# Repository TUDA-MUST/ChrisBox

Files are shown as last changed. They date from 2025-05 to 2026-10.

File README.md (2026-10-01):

# ChrisBox
(**CH**arge **R**eading **I**nferface **S**ystem Box)\
4-Channel Charge Amplifier PCB

## Introduction

Welcome to ChrisBox!\
ChrisBox is a four-channel charge amplifier, mainly developed for the simultaneous charge measurement of four ferroelectret sensors.
The main goals of the development were
- low noise (shielding concept),
- portability,
- usability,
- affordability.

More details about ChrisBox can be found [here](#about-chrisbox).

> [!IMPORTANT]
> This document describes the features and assembly of ChrisBox and does not provide guidance on constructing or using ferroelectret sensors.

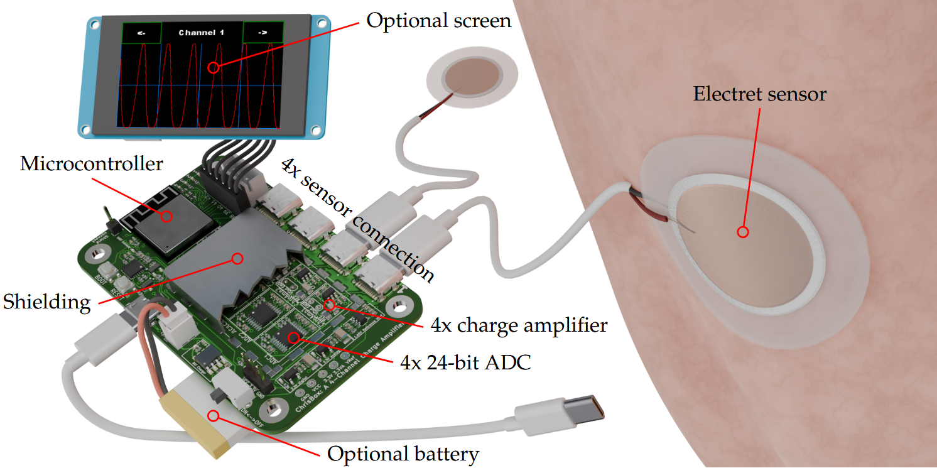
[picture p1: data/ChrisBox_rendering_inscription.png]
Rendered image of ChrisBox with display, battery and connected ferroelectret sensors.


## About this Repository

This repository contains the PCB design of ChrisBox, the CAD files for the Box, where the PCB can be combined with a battery and a display, as well as general code for the PCB.
- [PCB](/PCB) -> circuit board
- [CAD](/CAD) -> housing for the circuit board and an additional display
- [CODE](/CODE) -> code to be flashed on the microcontroller of the PCB, and code for a Nextion display.

A code description is found in the `./CODE` folder, if you just want to build a ChrisBox, the following instructions should be sufficient.

Ordering and Building instructions are included here:
- [ORDERING INSTRUCTIONS](/ORDERING_INSTRUCTIONS.md)
- [BUILDING INSTRUCTIONS](/BUILDING_INSTRUCTIONS.md)

Contributing to ChrisBox and this repository: [CONTRIBUTORS](#contributors).\
License: [LICENSE](/LICENSE).

Information about citation is found here: [CITATION](#citation).

## About ChrisBox

### Development objective and target group

Piezoelectric sensors convert electric charge in response to mechanical loading and are widely studied for their high sensitivity.
In particular, ferroelectret sensors provide the flexibility and material system design that enable biocompatibility.
These signals are typically captured using commercial electrometers or custom-built charge amplifiers to enable portability.
However, the latter often lack the precision and robustness against electromagnetic interference (EMI).
Therefore, we present a compact, four-channel portable measurement system specifically designed for charge-based force sensing with piezoelectric sensors, called ChrisBox.
The system has been developed at the **Measurement and Sensor Technology Group** at **Technische Universität Darmstadt**, Darmstadt, Germany.

The main goals of the development were:
- **Low noise:** achieved through a shielding concept that covers the PCB, the cable to the sensor, and, depending on the sensor, the sensor itself.
- **Portability:** a key advantage over traditional electrometers and oscilloscopes, enabling measurements on the human body while walking or performing other movements.
- **Usability:** the PCB is designed for users without expertise in PCB development or programming, allowing straightforward measurements with ferroelectret sensors.
- **Affordability:** one assembled PCB costs roughly 50 euros in 2025, facilitating reproduction and simultaneous use while avoiding the need for expensive laboratory instruments such as electrometers.

### Detailed decription of ChrisBox

**Analog electronics**
A ferroelectret is connected to the PCB via a USB-C cable and connector.
The signal wires, D+ and D-, carry the charge displacement generated by the ferroelectret, which is converted into a voltage signal by a charge amplifier.
An exemplary application of this setup is heart rate measurement, which requires low-frequency measurements.
Therefore, a large feedback resistor (in the G&Omega; range) is used in the charge amplifier.
A reference voltage at the midpoint of the measurement range (around 1.65 V) is provided to enable differential measurements within the 0–3.3 V range.
The analog electronics are replicated four times, with each channel operating independently.

**Digital electronics**
The output of each charge amplifier is connected to an ADC (ADS1220).
The reference voltage is also supplied to the ADC to enable differential measurements.
All four ADCs communicate with an ESP32 via SPI.

**ESP32**
An ESP32 S3 Mini 1 serves as the microcontroller of the ChrisBox, accompanied by Boot and Reset buttons.
A UART-to-USB converter ensures reliable connectivity with various PCs.

**Support circuits**
The PCB includes several additional circuits: four programmable status LEDs controlled by the ESP32, a UART connector for interfacing with a Nextion display, and a connector providing access to five GPIO pins of the ESP32 for custom functions.
A 5 V supply, switchable by the ESP32, can power the Nextion display.
A battery can be connected for power supply and is simultaneously charged when the board is connected to USB.

**Shielding**
The PCB is shielded by a metallic frame and cover, as well as an internal shielding layer within the board.
USB-C cables are used to connect the ferroelectret sensors, as they are both shielded and readily available.
Each ferroelectret sensor must be soldered to a USB-C connector.
Since an unshielded ferroelectret sensor can act as a source of noise, proper shielding is essential to ensure a low-noise measurement setup.

**Data output**
The acquired measurement data can be output in several ways:
- Serial communication to a PC,
- UART connection to a Nextion display for real-time visualization,
- ESP-NOW for wireless data transmission, requiring a second ESP32 as receiver for the data, which itself could communicate to a PC.

## Contributors

ChrisBox was developed at the [Measurement and Sensor Technology Group](https://www.etit.tu-darmstadt.de/must/) at Technische Universität Darmstadt, Germany, by:
- [Sven Suppelt](https://orcid.org/0000-0002-2338-9333)
- [Dominik Werner](https://orcid.org/0009-0001-8082-5584)
- [Alexander A. Altmann](https://orcid.org/0000-0001-5299-3620)
- [Felix Herbst](https://orcid.org/0000-0003-1480-3691)
- [Jan H. Dörsam](https://orcid.org/0000-0001-9807-6641)
- [Bastian Latsch](https://orcid.org/0000-0001-9929-5694)
- [Prof. Mario Kupnik](https://orcid.org/0000-0003-2287-4481)

## Citation

If you would like to reference the project, please cite DOI: [10.3390/hardware4040020](https://doi.org/10.3390/hardware4040020).

```
@article{hardware4040020,
  author = {Suppelt, Sven and Werner, Dominik and Altmann, Alexander Anton and Herbst, Felix and Ulmer, Lukas and Dörsam, Jan Helge and Latsch, Bastian and Kupnik, Mario},
  title = {ChrisBox: An Open-Source 4-Channel Portable Charge Amplifier for Research and Education},
  journal = {Hardware},
  year = {2026},
  volume = {4},
  number = {4},
  pages = {20},
  doi = {10.3390/hardware4040020}
}
```

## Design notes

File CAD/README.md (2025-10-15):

# CAD

Welcome to the CAD folder!
Here can basically every physical part of a ChrisBox assembly be found. The assembly is shown below.
The CAD is made with Siemens NX, and STL data is provided, e.g. for 3D printing.

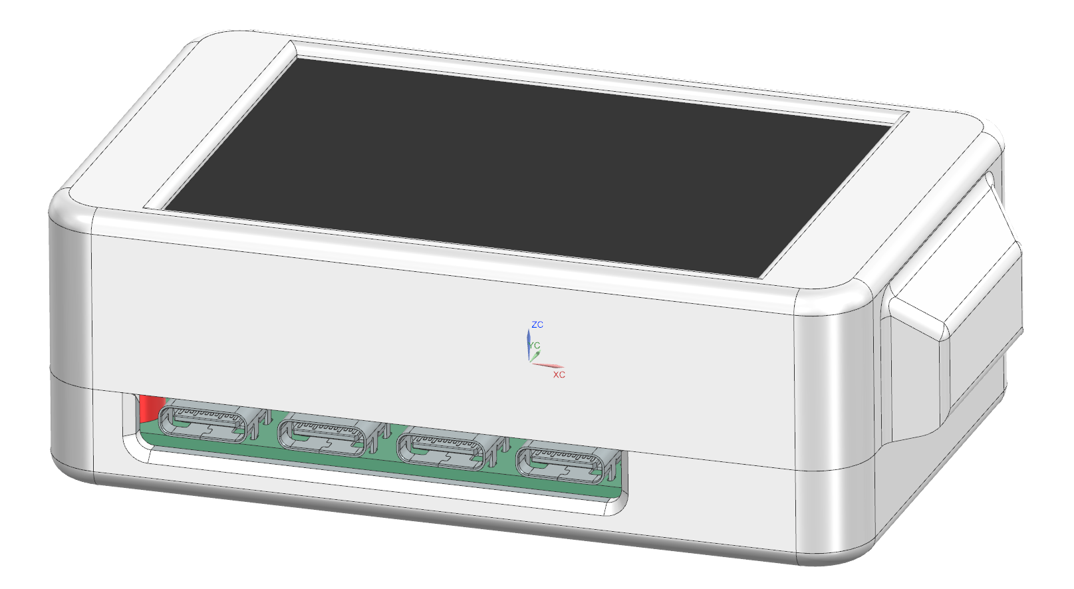
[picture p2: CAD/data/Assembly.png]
Screenshot of a ChrisBox Assembly


## Content of the CAD folder

- `./Casing` - Siemens NX part files for the casing.
- `./Electric` - Electric components of the assembly (PCB with most components, a standard Battery and the NX3224K024 display). 
- `./STLs` - STL data of the casing, e.g. for 3D printing
- `./data` - pictures of the assembly

## Building the casing

For building instructions refer to [BUILDING INSTRUCTIONS](/BUILDING_INSTRUCTIONS.md).

## Alternate Version without the Nextion screen

If you are only interested in a Chrisbox without a display, you will find a protective case for the PCB in the “00_VersionWithoutScreen” folder. 
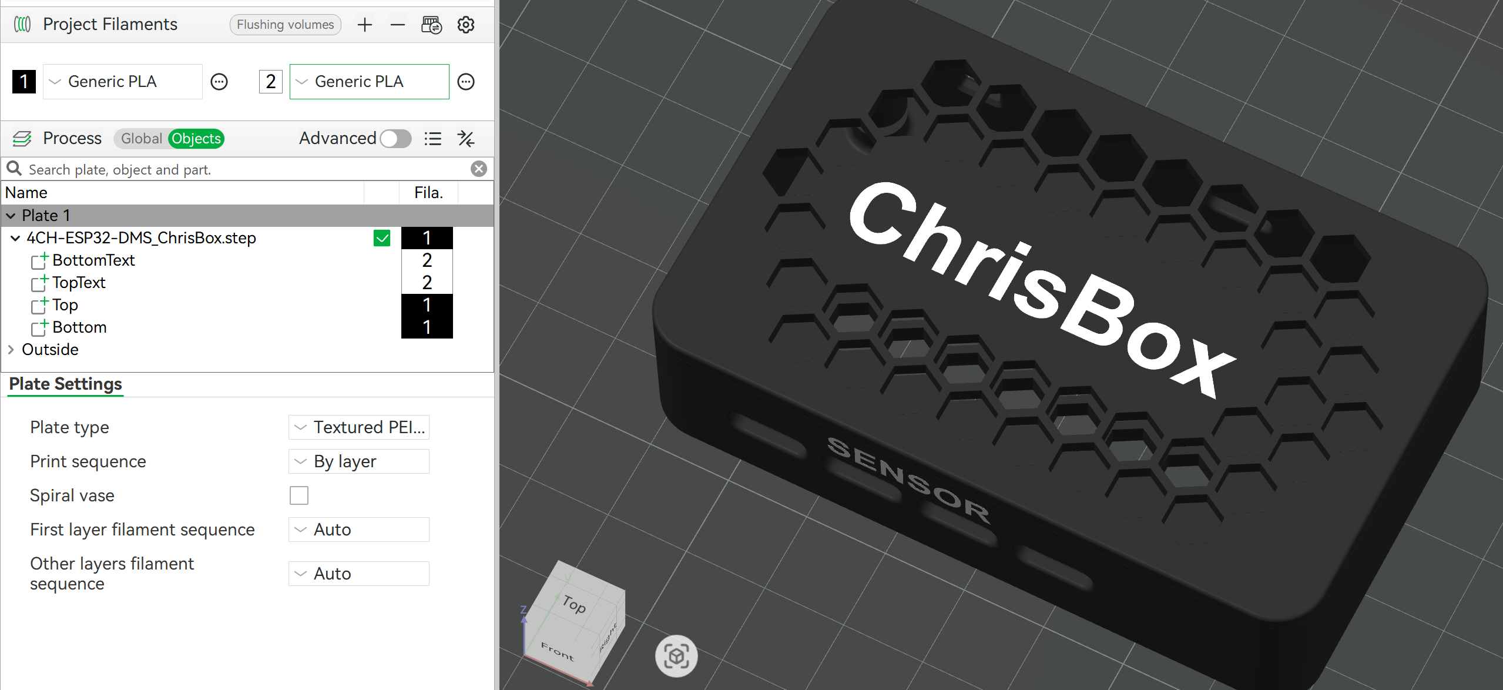
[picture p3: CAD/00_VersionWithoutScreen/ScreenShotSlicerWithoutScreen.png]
Screenshot of a ChrisBox Assembly wihtout a screen


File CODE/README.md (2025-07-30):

# Code

Welcome to the Code folder of ChrisBox!
The code for ChrisBox was written in the Arduion IDE.

## Content of the PCB folder

- `./ChrisBox_Code` - The code and librarys for the ChrisBox PCB.
- `./Nextion Code` - The code/program for the Nextion display.

## Flashing the code on the PCB

For flashing both the PCB and the Nextion display, please refer to [BUILDING INSTRUCTIONS](/BUILDING_INSTRUCTIONS.md).

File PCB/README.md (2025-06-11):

# PCB

Welcome to the PCB folder of ChrisBox!
The ChrisBox PCB is designed with KiCad. The Project files and generated Exports are found here.

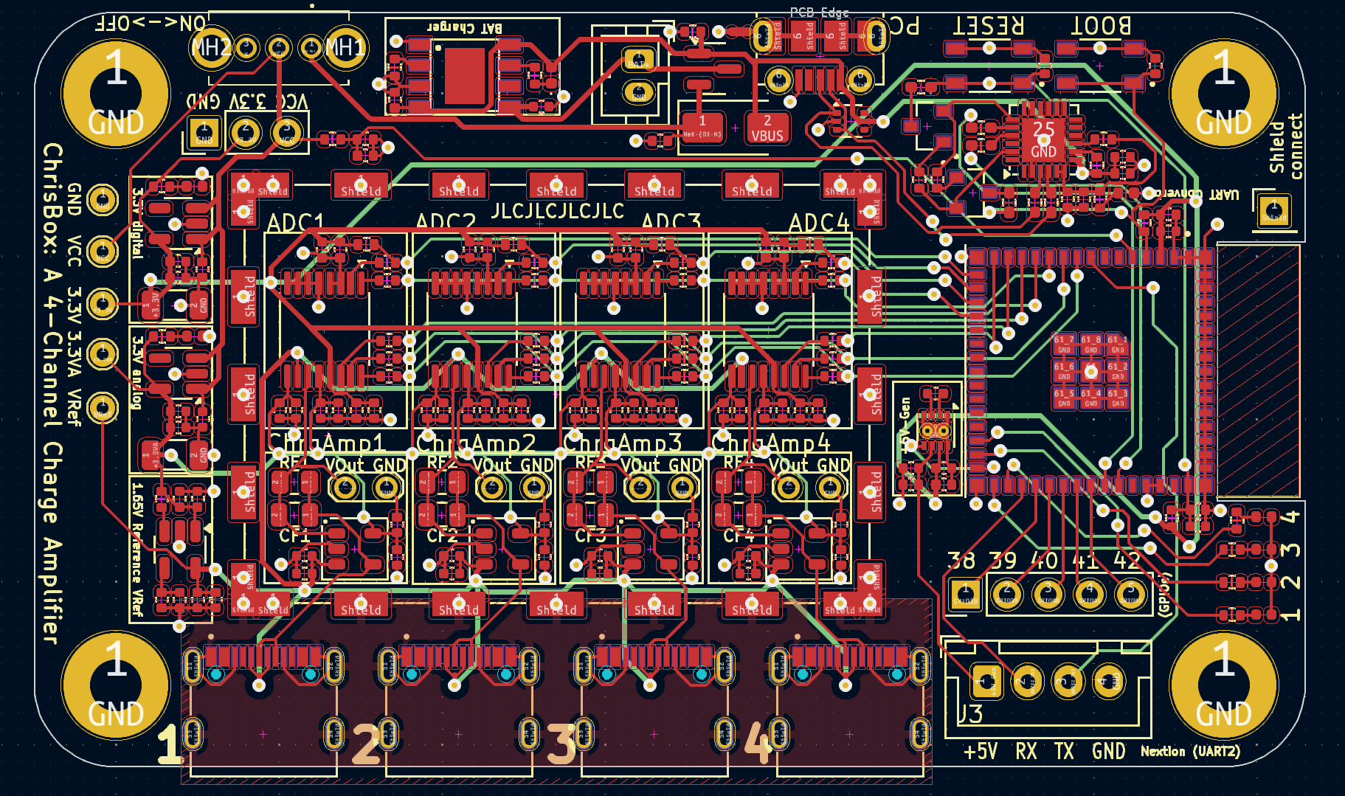
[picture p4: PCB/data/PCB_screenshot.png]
Screenshot of a ChrisBox Assembly


## Content of the PCB folder

- `./data` - pictures of the PCB and some for the schematic and silkscreen.
- `./exports` - The `.step`-export of the ChrisBox PCB.
- `./interactive bom` - The interactive HTML BOM (made with Interactive Html Bom). It is useful for handsoldering or just looking up which component has to go where.
- `./jlcpcb` - Output data from the KiCAD JLCPCB tools. This data can be used for ordering a PCB with components. Always re-check the data yourself!
- `./models` - Additional footprints and models, which are not included in KiCad and its plugins itself.

The other files in this folder are the [main KiCad project](/PCB/ChrisPCB.kicad_pro) with schematic and pcb, as well as the sub-schematics (ferro_amplifier and usb_connector).

## Notes on KiCad settings

The design was made with KiCad 8.0. Installed plugins are the Alternate KiCad Library (by Dawid Cislo), the Interactive Html Bom (by qu1ck) and the KiCAD JLCPCB tools (by Bouni).
Additional Footprints or 3D models are found in the `./models` folder.\
Always check the JLCPCB options yourself! The tools seemed to "forget" some data from time to time.

## Ordering and building the PCB

For ordering instructions refer to [ORDERING INSTRUCTIONS](/ORDERING_INSTRUCTIONS.md).
For building instructions refer to [BUILDING INSTRUCTIONS](/BUILDING_INSTRUCTIONS.md).

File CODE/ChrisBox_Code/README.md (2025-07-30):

# ChrisBox Code

In this section the main features of the ChrisBox code are explained. The code was written in Arduino IDE 2.x.x.

> [!NOTE]
> In the code the [Protocentral library for the ADS1220](https://github.com/Protocentral/Protocentral_ADS1220) is used, which also is under the MIT license. Some minor changes are made in the library to adapt the pins to the wiring of the ChrisBox PCB.

## Code structure

There are the following sections in the code:

- include for the used libraries
- definitions for pins
- some settings and constants. Settings regarding ESP NOW, UART, BAUDRate etc. are made here.
- variables, which are used at runtime
- setup for ESP NOW
- setup for UART
- void setup(). The different parts (e.g. UART) are started here, if the part is wished (see settings and constants).
- void loop(). This is repeated after the setup until the power is switched of or reset is pressed. The ADCs are read and the measured values published on the Serial port, ESP NOW and/or UART
- support functionality

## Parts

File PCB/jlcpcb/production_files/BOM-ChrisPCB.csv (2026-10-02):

Comment | Designator | Footprint | LCSC | Quantity
0 | R38,R39,R41,R42,R45,R50 | R_0402_1005Metric_Pad0.72x0.64mm_HandSolder | C17168 | 6
100n | C10,C12,C13,C18,C2,C21,C22,C23,C26,C27,C30,C33,C34,C35,C38,C39,C4,C42,C45,C46,C47,C50,C51,C54,C57,C58,C59,C6,C62,C63,C65,C67,C71,C79,C81,C9 | C_0402_1005Metric | C1525 | 36
100u | C7,C8 | C_1206_3216Metric | C15008 | 2
10k | R40,R44,R47,R49,R52,R6,R7 | R_0402_1005Metric | C25531 | 7
10u | C1,C11,C14,C16,C17,C19,C20,C24,C25,C28,C29,C3,C31,C32,C36,C37,C40,C41,C43,C44,C48,C49,C5,C52,C53,C55,C56,C60,C61,C64,C69,C70,C73,C75,C77,C80 | C_0402_1005Metric | C15525 | 36
1k | R12,R18,R24,R30,R37,R43,R48 | R_0402_1005Metric | C11702 | 7
1u | C15,C72,C74,C76,C78 | C_0402_1005Metric | C14445 | 5
2G | RF1,RF2,RF3,RF4 | R_0805_2012Metric | C2484710 | 4
360p | CF1,CF2,CF3,CF4 | C_0805_2012Metric | C5375895 | 4
4.7u | C66,C68 | C_0402_1005Metric | C23733 | 2
47 | R13,R14,R15,R16,R17,R19,R20,R21,R22,R23,R25,R26,R27,R28,R29,R3,R31,R32,R33,R34,R35 | R_0402_1005Metric | C25118 | 21
470 | R1,R2,R36,R4,R5,R51,R53 | R_0402_1005Metric | C25117 | 7
4k7 | R46 | R_0402_1005Metric | C25900 | 1
AD8605ARTZ | U10,U4,U6,U8 | SOT-23-5 | C9641 | 4
ADS1220xPW | U3,U5,U7,U9 | TSSOP-16_4.4x5mm_P0.65mm | C48263 | 4
AP2112K-3.3 | U13,U14 | SOT-23-5 | C51118 | 2
BOOT_SWITCH | S2 | SW_SKRPABE010 | C778166 | 1
CP2102N-Axx-xQFN24 | U12 | QFN-24-1EP_4x4mm_P0.5mm_EP2.6x2.6mm | C969151 | 1
Conn_01x04_Socket | J3 | JST_XH_B4B-XH-A_1x04_P2.50mm_Vertical | C144395 | 1
DMG2305 | Q3 | SOT-23 | C2940629 | 1
D_Schottky | D1 | D_SMA | C163541 | 1
ESP32-S3-MINI-1-N8 | U2 | XCVR_ESP32-S3-MINI-1-N8 | C3013941 | 1
JST-PH | X1 | JST_PH_B2B-PH-K_1x02_P2.00mm_Vertical | C131337 | 1
LED_CHRG | D9 | LED_0402_1005Metric | C2852592 | 1
LED_INFO1 | D5 | LED_0402_1005Metric | C434449 | 1
LED_INFO2 | D6 | LED_0402_1005Metric | C434449 | 1
LED_INFO3 | D7 | LED_0402_1005Metric | C2844007 | 1
LED_INFO4 | D8 | LED_0402_1005Metric | C2844007 | 1
LED_PWR1 | D2 | LED_0402_1005Metric | C2852592 | 1
LED_PWR2 | D3 | LED_0402_1005Metric | C2852592 | 1
LED_PWR3 | D4 | LED_0402_1005Metric | C2852592 | 1
LM2775DSG | U15 | WSON-8-1EP_2x2mm_P0.5mm_EP0.9x1.6mm_ThermalVias | C473361 | 1
RESET_SWITCH | S3 | SW_SKRPABE010 | C778166 | 1
RFShield_TwoPieces | J6 | Laird_Technologies_BMI-S-205-F_38.10x25.40mm_HandSolder_SelfMade | C7429170 | 1
SK-12D02-VG3 | S1 | SK12D02VG3 | C136723 | 1
SS8050-G | Q1,Q2 | TRANS_SS8050-G | C164886 | 2
TP4056 | IC1 | SOP-8 | C16581 | 1
TPS73616DBV | U1 | SOT-23-5 | C115797 | 1
TYPE-C-31-M-12 | J10,J7,J8,J9 | HRO_TYPE-C-31-M-12 | C165948 | 4
USBLC6-2P6 | U11 | SOT-666 | C2827693 | 1
USB_B_Micro | J11 | USB_Micro-B_Molex-105017-0001 | C505111 | 1
Conn_01x05_Pin | J2 | PinHeader_1x05_P2.54mm_Vertical |  | 1
TestPoint | TP1 | TestPoint_THTPad_D1.5mm_Drill0.7mm |  | 1
TestPoint | TP5 | TestPoint_THTPad_D1.5mm_Drill0.7mm |  | 1
TestPoint | TP3 | TestPoint_THTPad_D1.5mm_Drill0.7mm |  | 1
Conn_01x01_Pin | J5 | PinHeader_1x01_P2.54mm_Vertical |  | 1
Conn_01x03_Pin | J1 | PinHeader_1x03_P2.54mm_Vertical |  | 1
TestPoint | TP4 | TestPoint_THTPad_D1.5mm_Drill0.7mm |  | 1
TestPoint | TP2 | TestPoint_THTPad_D1.5mm_Drill0.7mm |  | 1

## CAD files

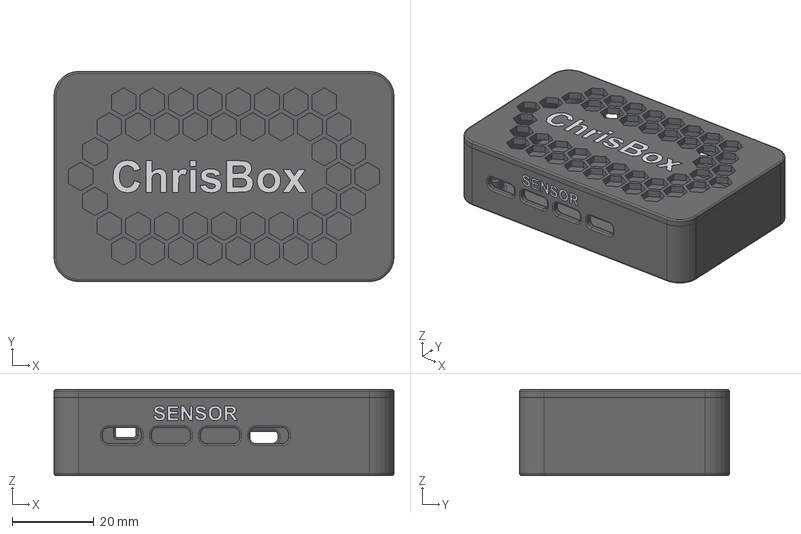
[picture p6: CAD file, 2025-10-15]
CAD/00_VersionWithoutScreen/4CH-ESP32-DMS_ChrisBox.step
83.0 x 51.3 x 21.0 mm
BottomText
TopText
Top
Bottom

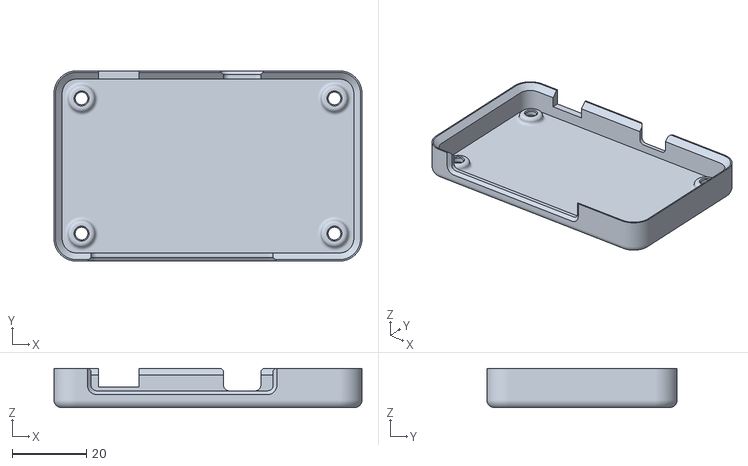
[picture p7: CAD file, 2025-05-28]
CAD/STLs/Casing_Bottom.stl
82.8 x 51.1 x 10.5

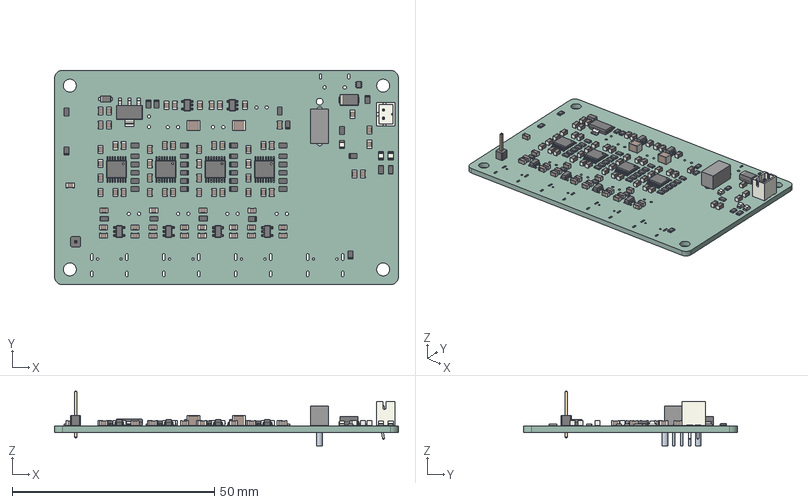
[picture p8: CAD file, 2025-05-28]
PCB/exports/ChrisPCB.step
85.0 x 53.0 x 13.5 mm
R_0805_2012Metric x 40
C_1210_3225Metric x 2
ASSEMBLY
SOT_23_5 x 6
C_0805_2012Metric x 69
D_SMA
TSSOP_16_44x5mm_P065mm x 4
LED_0805_2012Metric x 3
SOT_666
SOT_223
D_SOD_123F
JST_B2B_PH_K
PinHeader_1x01_P254mm_Vertical
Platine 4 Kanal Ferroelektret_PCB

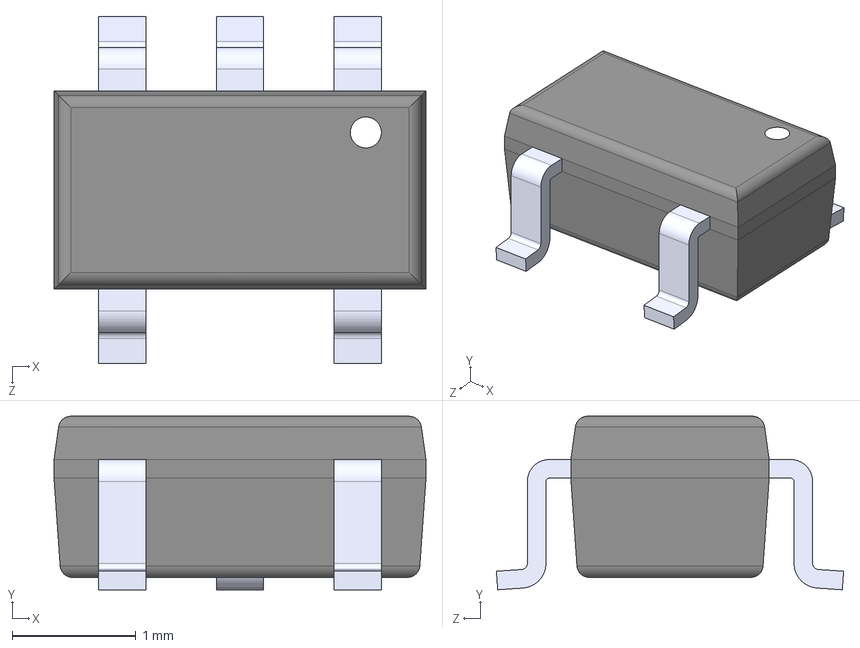
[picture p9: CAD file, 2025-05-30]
PCB/models/AP2112K-3.3TRG1/AP2112K-3.3TRG1.step
3.00 x 1.40 x 2.80 mm

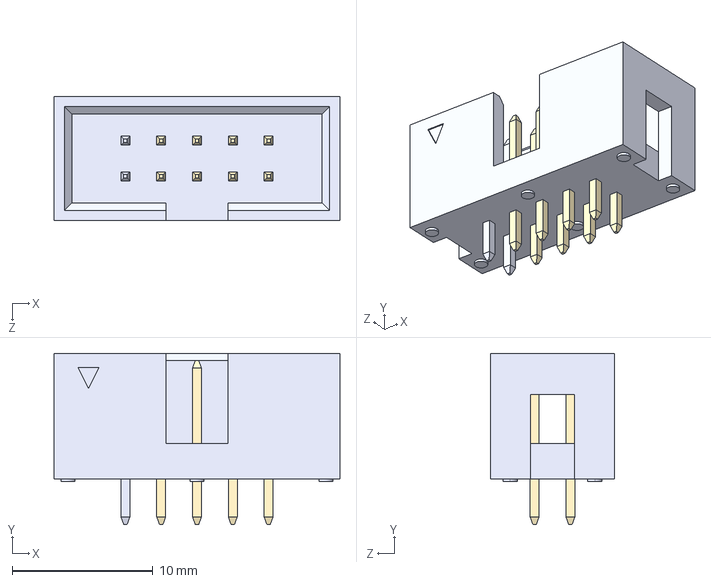
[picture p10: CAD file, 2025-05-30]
PCB/models/DC3 10P/302-S-10-D1R1.step
20.3 x 12.2 x 8.80 mm

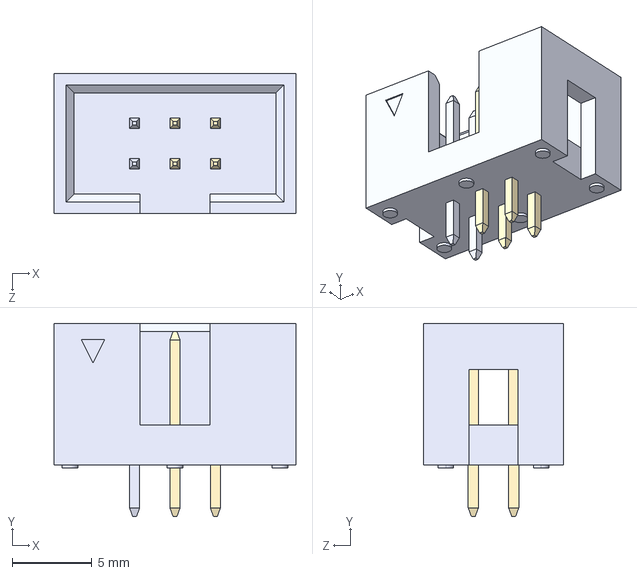
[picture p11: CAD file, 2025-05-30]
PCB/models/DC3 6P/302-S-06-D1R1.step
15.2 x 12.2 x 8.80 mm

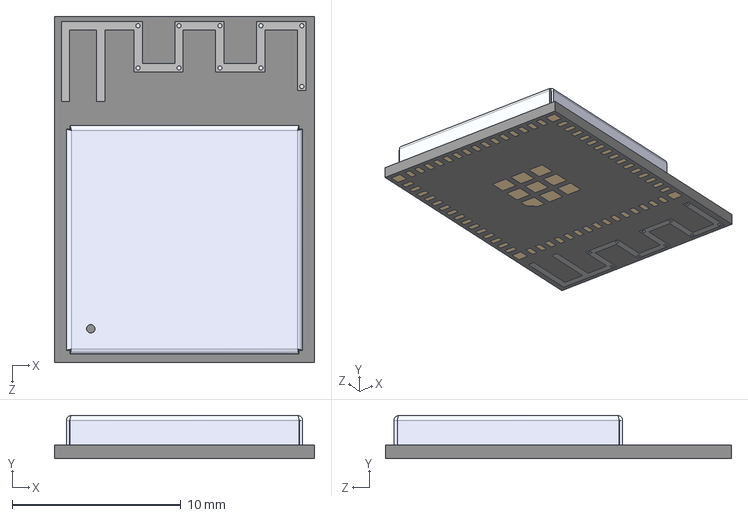
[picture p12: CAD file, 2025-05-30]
PCB/models/ESP32-S3-MINI-1-N8/ESP32-S3-MINI-1-N8.step
15.4 x 2.55 x 20.5 mm

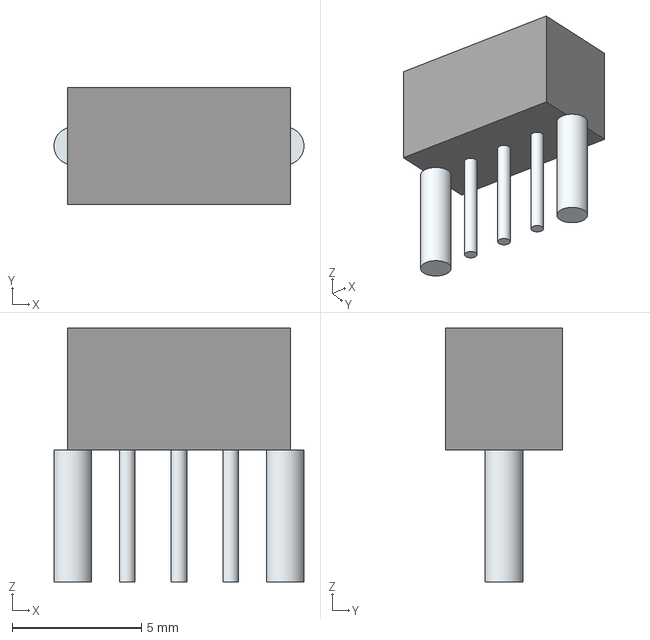
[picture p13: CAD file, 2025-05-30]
PCB/models/SK-12D02-VG3/SK-12D02-VG3.stp
9.65 x 4.50 x 9.80 mm
Leads x 5

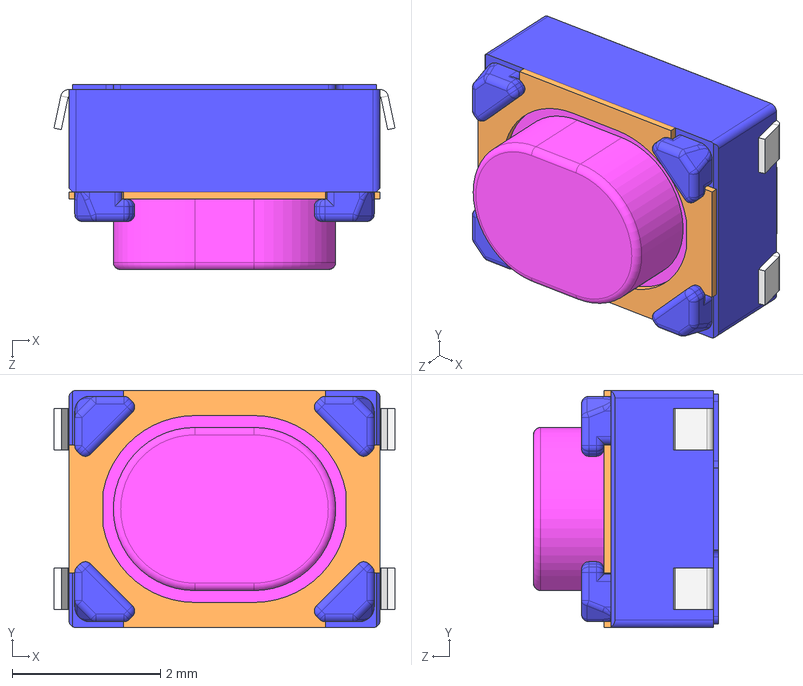
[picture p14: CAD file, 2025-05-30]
PCB/models/SKRPAB.STEP
4.60 x 3.20 x 2.50 mm

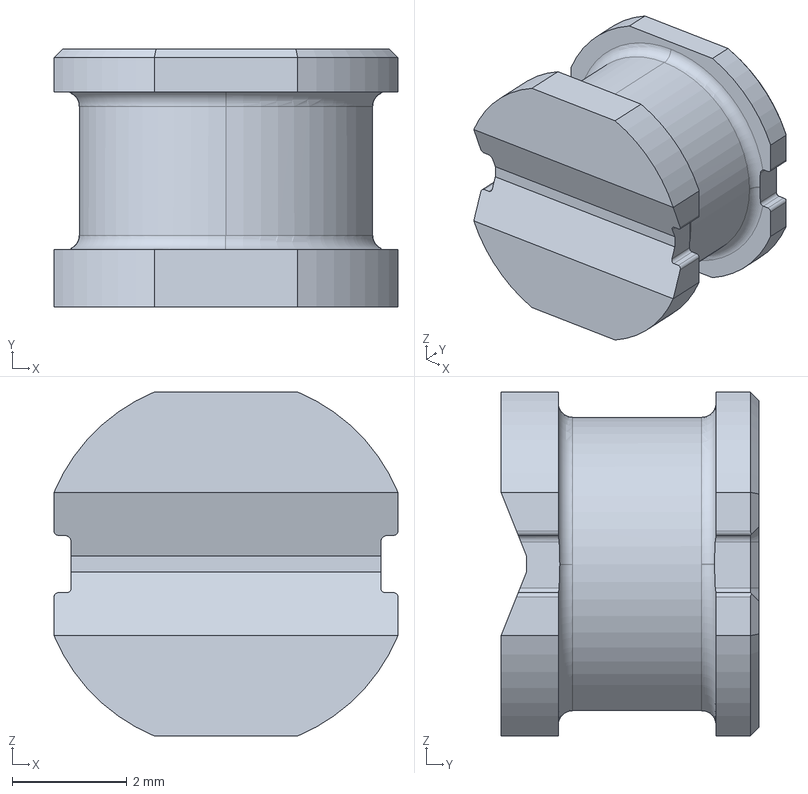
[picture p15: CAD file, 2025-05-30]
PCB/models/SRN6045-330M/SRN6045-330M.step
6.00 x 4.50 x 6.00 mm

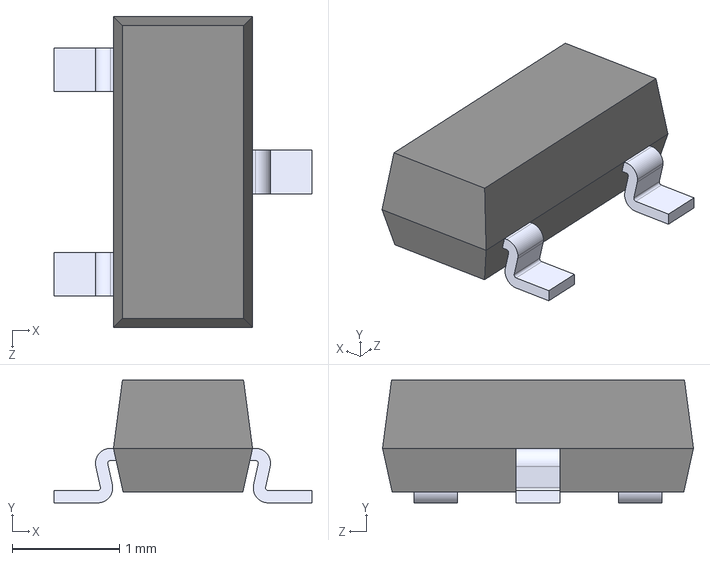
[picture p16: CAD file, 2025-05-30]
PCB/models/SS8050-G/SS8050-G.step
2.40 x 1.14 x 2.90 mm

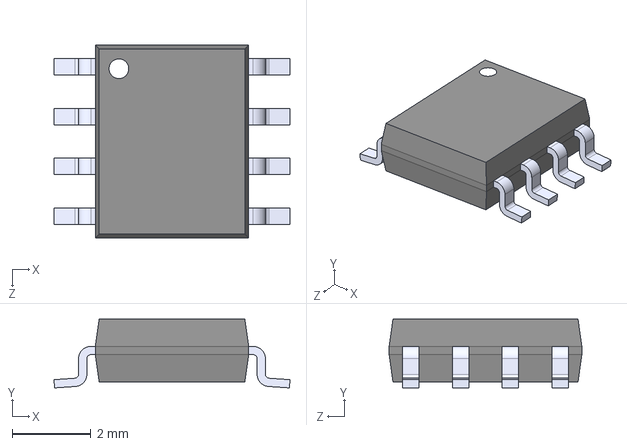
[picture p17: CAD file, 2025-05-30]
PCB/models/TP4056/TP4056.step
6.00 x 1.75 x 4.90 mm

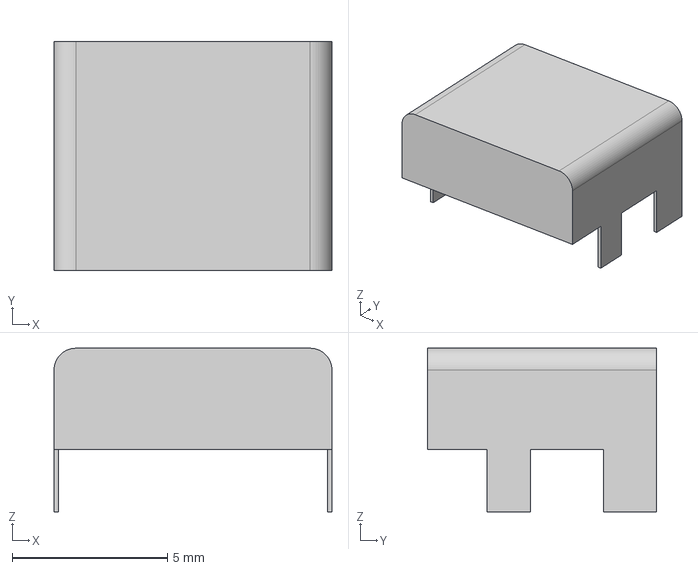
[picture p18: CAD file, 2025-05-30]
PCB/models/TYPE-C-31-M-12/TYPE-C-31-M-12 v1.step
8.94 x 7.35 x 5.26 mm

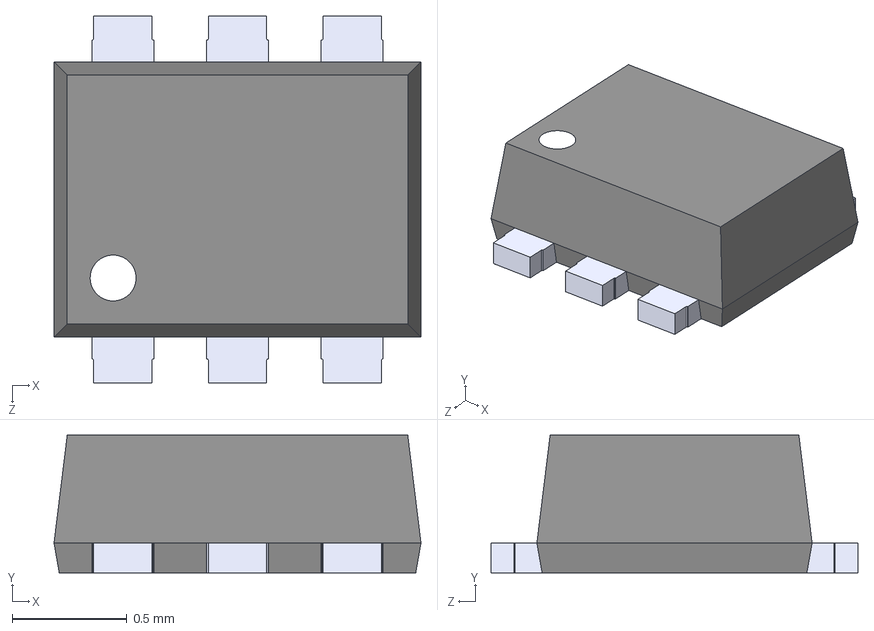
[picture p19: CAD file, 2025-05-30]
PCB/models/USBLC6-2P6/USBLC6-2P6.step
1.60 x 0.6 x 1.60 mm

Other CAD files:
PCB/models/SKRPABE010/SKRPABE010.step
CAD/STLs/Spacer.stl
PCB/models/TYPE-C-31-M-12--3DModel-STEP-56544.STEP
PCB/models/TYPE-C-31-M-12/TYPE-C-31-M-12.step
CAD/STLs/Casing_Top.stl
PCB/models/BMI-S-230-F-R.STEP
PCB/models/Molex USB 1050170001/1050170001.stp
PCB/models/TP4056-42-ESOP8.STEP

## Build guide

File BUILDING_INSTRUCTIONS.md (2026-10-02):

# Building Instructions

This are the building instructions for a complete ChrisBox setup. A complete setup includes not only the main PCB and its software, but also a Nextion display and a casing. The display and casing are optional for functionality.

1. [PCB Hardware](#pcb-hardware)
2. [PCB Software](#pcb-software)
3. [Nextion Software](#nextion-software)
4. [Full ChrisBox Assembly](#full-chrisbox-assembly)

## PCB Hardware

When ordering a populated circuit board (e.g. from JLCPCB), the result should look like this:

Unsoldered version of ChrisBox

This PCB is not finished.
The shielding frame and G&Omega; feedback resistors for the charge amplifiers are typically not in stock at JLCPCB.
If you did not use their Global Sourcing Parts Service, these components are not assembled and have to be placed by hand:
- Feedback resistors: 4x 0805 (in) or 2012 (mm), 5G&Omega;
- Shield frame: 1x Laird Technologies, BMI-S-205-F
- Shield cover: 1x Laird Technologies, BMI-S-205-C

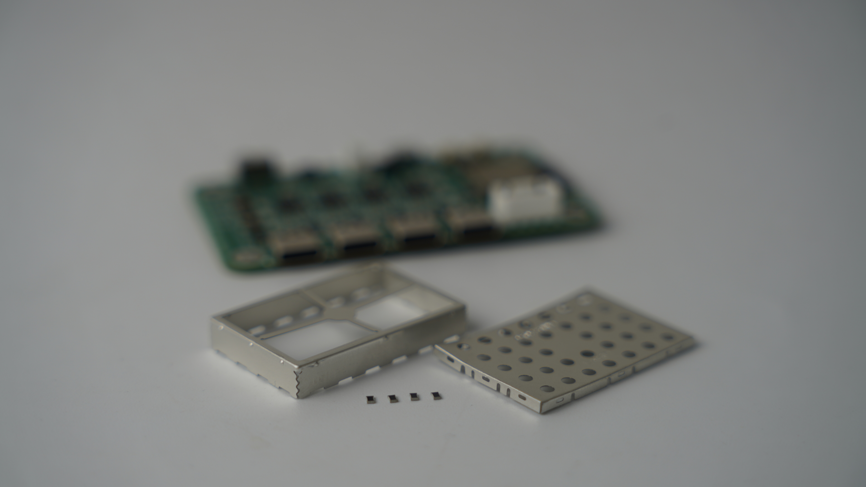
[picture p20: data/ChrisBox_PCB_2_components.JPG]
ChrisBox components for soldering


The places for the feedback resistors and the shielding frame are shown in the picture below. The shielding cover does not have to be soldered, it can be placed on the fence afterwards.
> [!TIP]
> Things get easier if the resistors are soldered first because of the height of the components.
> Also it can come handy to remove the cross in the middle of the shielding frame before soldering if some components have to be reached afterward.

Unfortunately, the frame and connected shielding plane (in the PCB) are good in heat distribution.
Therefore it takes a while to heat the pads and solder the frame.

> [!WARNING]
> When soldering, try to use as little flux as possible and/or clean the circuit board afterward. Flux is slightly conductive and distorts the sensor values, which can result in saturation of the ADC inputs!

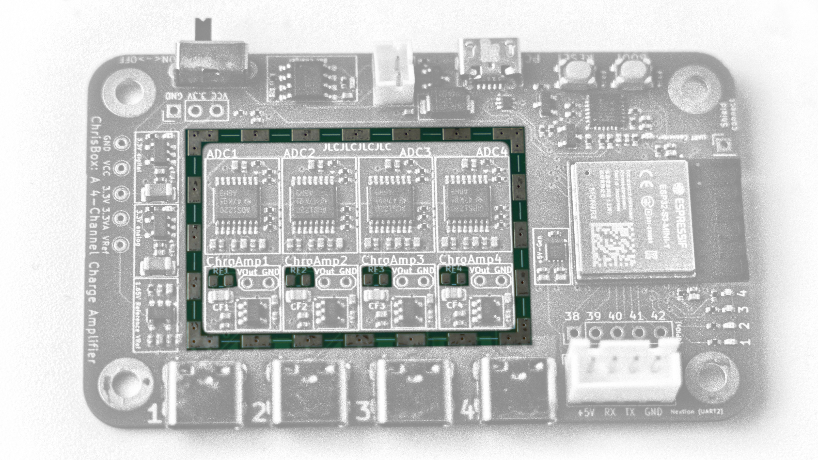
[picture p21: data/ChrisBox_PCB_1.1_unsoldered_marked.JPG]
ChrisBox places of soldering


The soldered resistors and frame can look like in the picture below. The soldering part of the PCB is finished now!

Soldered version of ChrisBox

## PCB Software

On the PCB is an ESP32-S3 microcontroller (ESP32-S3-MINI-1). The connection between PC and microcontroller works with a UART-TO-USB bridge (CP2102N). This is the same bridge chip as on most ESP32 development boards. To enable interaction between a PC and the microcontroller on the ChrisBox PCB, the **Silicon Labs CP210x USB to UART Bridge** driver should be installed on the PC.
After installing the driver, connect the ChrisBox PCB to the PC via micro USB cable and turn it on with the switch on the side. Before turing on one LED should work, after turning on multiple LEDs.
The PC should detect a device called something like "Silicon Labs CP210x USB to UART Bridge" on a COM port. Remember this COM port!

Programming works with the **Arduino IDE**. Programming and the setting were tested with Arduino IDE 2.3.6, but other versions should work as well.
In the Arduino IDE, select the device as in the picture below. Select the COM port accordingly to the one your PCB is connected to.
It may be necessary to install the esp32 by Espressif Systems via the Boards Manager.

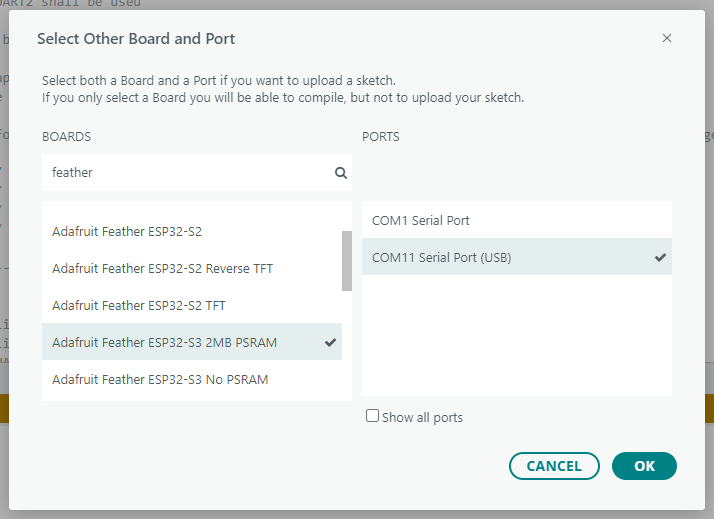
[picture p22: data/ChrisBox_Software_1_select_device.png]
Arduino IDE select device


Open the downloaded code in the Arduino IDE. It is important that all code files from this repository are in the same folder after downloading, that the Arduino IDE can find libraries while compiling.
Select the upload options as shown below and hit upload. This can take a while. After finishing, the ESP reboots and the uploaded program starts. While a program is running, a LED is blinking on the PCB.
You can see measurement data incoming on the serial monitor (select baud rate 115200). This serial data also can be viewed in the **Better Serial Plotter** or tools like **MATLAB**.

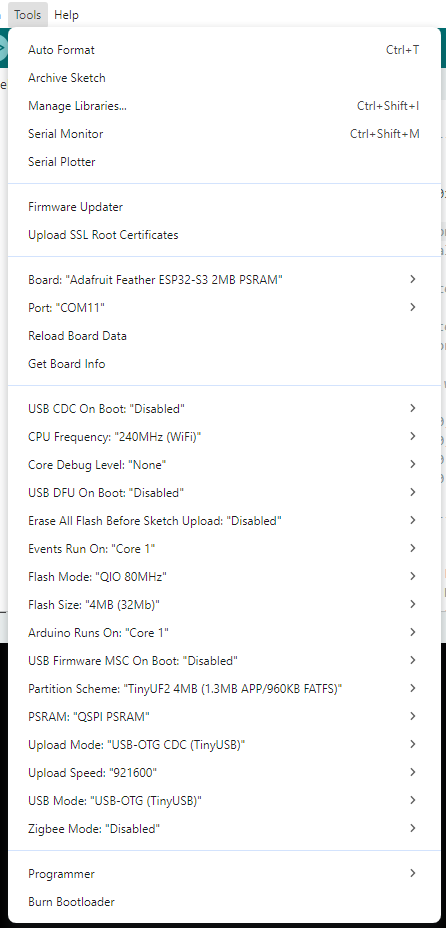
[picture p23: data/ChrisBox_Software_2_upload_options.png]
Arduino IDE upload options


## Nextion Software

The used Nextion display is a NX3224K024 display. The `.HMI` file with the code for the Nextion Editor is in the `./CODE` folder, as well a the `.tft` file. This `ChrisBox Nextion.tft` file can be flashed on a NX3224K024 display via micro SD card.
Either you open the `.HMI` file in Nextion Editor and execute a TFT file output, or you just take the given `.tft` file:
1. Save the `.tft` file to a fresh micro SD card.
2. Insert this micro SD card into the Nextion display.
3. turn on power for the display (by connection GND and 5V, either to the USB adapter or to the ChrisBox PCB.)
4. Software update starts automatically, wait for finish.
5. Turn off the power.
6. Remove SD card.
7. The update is complete. By turning power on again the loaded program should be active, without SD card!

## Full ChrisBox Assembly

The full ChrisBox assembly consists of:
- ChrisBox PCB with shielding cover
- Nextion NX3224K024 display
- cable between PCB and display
- 1x Casing Top (3D printing)
- 1x Casing Bottom  (3D printing)
- 4x Spacer (3D printing)
- 4x M3x25 screw
- 4x Threaded insert M3x3,0 (CAD made for: hole diameter 4mm, blind hole depth min. 4mm)

ChrisBox Assembly parts overview

First, insert the threaded inserts into the top of the casing with a solder iron or threaded insert heat press.

<p align="center">
      
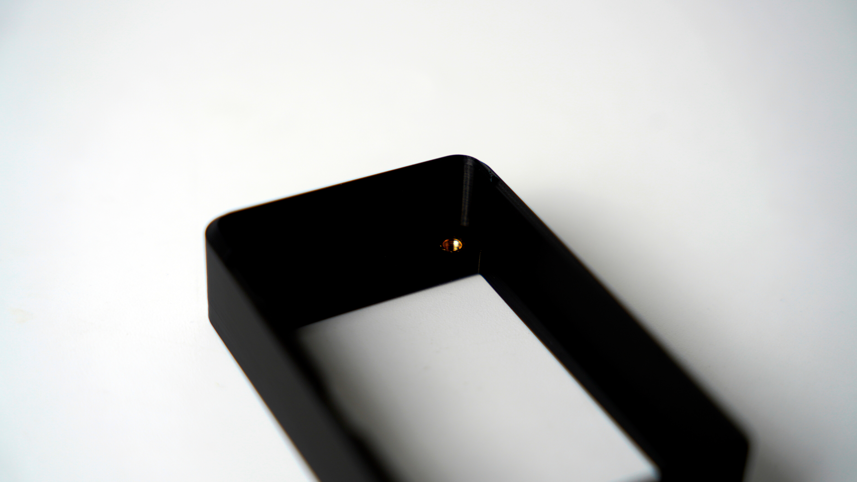
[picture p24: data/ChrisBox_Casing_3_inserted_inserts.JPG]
      
</p>

Then connect the Nextion display to the ChrisBox PCB. An ordered Nextion display contains a cable with on JST XH connector (the white 4x1 connector) and four Dupont connectors (the black 1x1 connectors).
Connect the JST XH connector to the display. You can connect the Dupont cables on the ChrisBox PCB, or you can shorten the cables and add crimp connections for another JST XH connector. This is what is used here on the picture. The JST XH connector fits directly onto the ChrisBox PCB.
Anyway, connect GND to GND, 5V to 5V and RX to TX and the other way around.
Place the shielding cover onto the shielding frame on the PCB.

Place the display into the top half of the casing, with the connector in the direction of the bulge.

<p align="center">
      
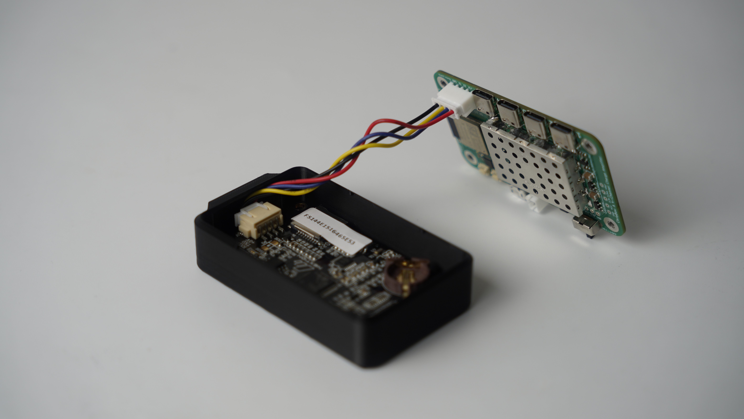
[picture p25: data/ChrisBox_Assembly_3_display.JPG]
      
</p>

Place the PCB into the bottom half of the casing, with screws and spacers.

Then connect both halves of the casing and tighten the screws. The ChrisBox is finished!

> [!TIP]
> Place the top half on top of the lower half with the screws and spacers on a table. Then move the assembly to the edge of the table that one screw can be tightened. Repeat for the other screws.

<p align="center">
      
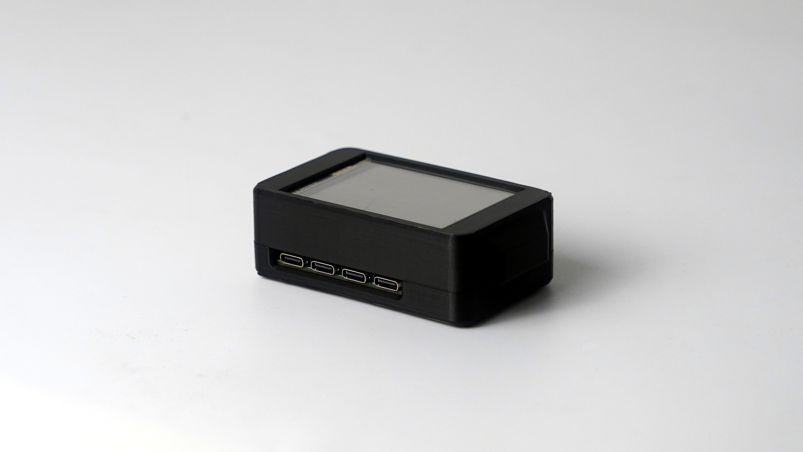
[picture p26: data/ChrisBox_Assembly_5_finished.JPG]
      
</p>

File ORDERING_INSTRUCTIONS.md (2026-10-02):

# Ordering Instructions

In this document information about the ordering process of various components can be found. This is segmented in the core PCB, required components for the PCB and additional material for a full ChrisBox setup.
It is recommended to read the other documents in this repository before ordering, as provided explanations about the different components ensure understanding of the ChrisBox and help avoiding mistakes in the ordering process.

- [README](/README.md)
- [BUILDING INSTRUCTIONS](/BUILDING_INSTRUCTIONS.md)

## PCB

The PCB is designed for ordering at JLCPCB.
Files are prepared for a populated PCB.
These files are made with the [JLCPCB Tool](https://github.com/bouni/kicad-jlcpcb-tools) in KiCad.
Keep in mind that not all components on the PCB are in stock at JLCPCB, so they have to be ordered separately (feedback resistors and shield).
Those parts can either be shipped by you to JLCPCB in advance using their [Global Sourcing Parts Service](https://jlcpcb.com/help/article/how-to-use-jlcpcb-global-sourcing-parts-service) or be manually assembled afterward, as described in the [building instructions](/BUILDING_INSTRUCTIONS.md).

The files are found in `./PCB/jlcpcb`. The gerber-files contain information about the raw PCB, the production-files contain the information about components and their positions on the PCB. The ordering process should look similar to the following screenshots:

> [!NOTE]
> The voltage generation for VRef (U1) is planned to be 1.6V in the schematic. In the JLCPCB tool and therefore in the exported data a 1.8V model is used due to production capability (at the time of data export). A reference voltage apart from 1.65V is no problem due to the differential measurement, but is shifts the measurement range so that "zero" is not in the middle and more positive or negative values can be measured.

<p align="center">
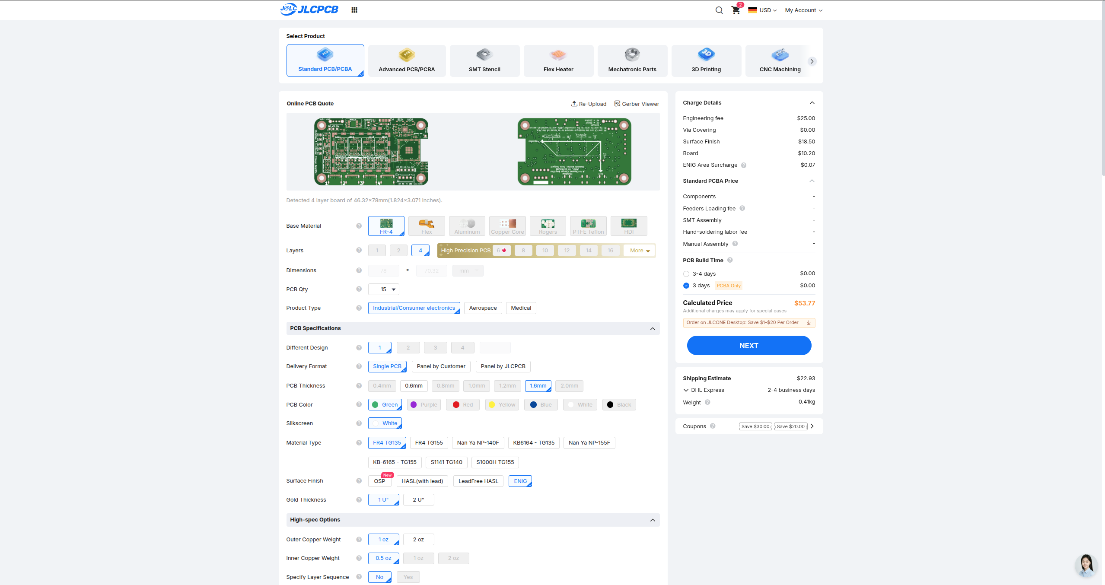
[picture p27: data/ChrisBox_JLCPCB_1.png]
      
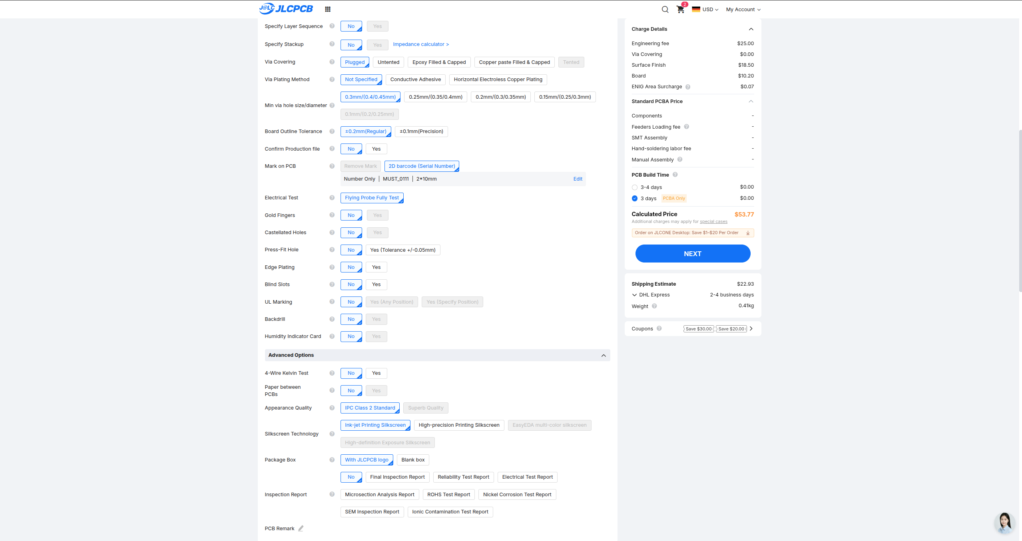
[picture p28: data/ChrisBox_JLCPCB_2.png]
      
</p>

In the ordering process, select the option "Mark on PCB", "2D Barcode (Serial Number)", "Number Only", and "Specify Position" if you want to place a serial number on your PCB.
The silkscreen contains a 2x10mm square for this purpose.
The older order number setting has been superseded.
More information about this topic can be found in the [JLCPCB instructions on PCB marks](https://jlcpcb.com/help/article/How-to-mark-on-PCB).

<p align="center">
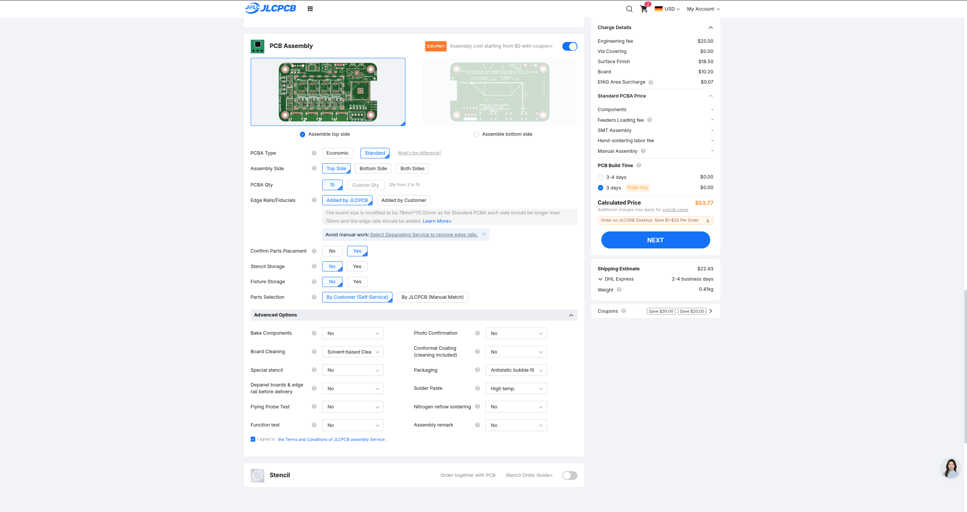
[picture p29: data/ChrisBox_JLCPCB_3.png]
      
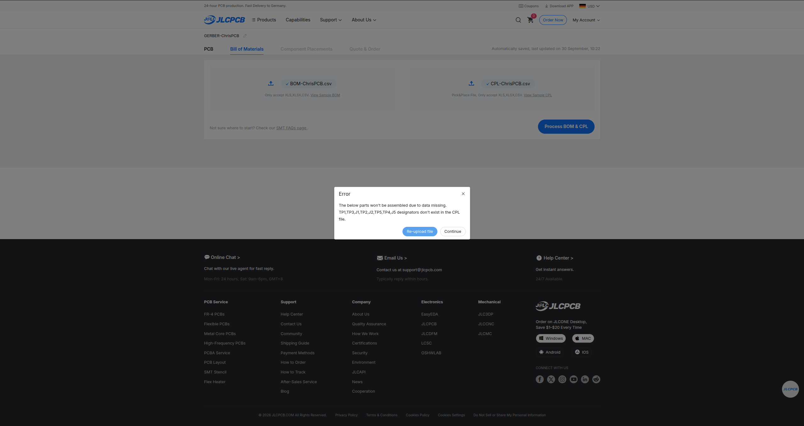
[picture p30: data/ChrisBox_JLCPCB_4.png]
      
</p>

You can also choose Economic PCBA Type here.
However, it may be possible that you are required to upgrade in the next steps.

A few optional solder headers (J1, J2, J5) and test points (TP1-TP5) purposely create an error during BOM/CPL processing, as they are part of the BOM but not in the CPL file.
Furthermore, a few lines in the BOM create warnings.
You will want to manually select all components in the list.
At the time of ordering, placement of the ESP32 module requires an upgrade from Economic to Standard Assembly.
You will need to confirm this message as well.
> [!NOTE]
> Please note that all parts have been pre-ordered through JLCPCBs [Global Sourcing Parts Service](https://jlcpcb.com/help/article/how-to-use-jlcpcb-global-sourcing-parts-service) in the screenshots.
> If you did not do so, the G&Omega; feedback resistors and shield will most likely not be available and cannot be placed.

<p align="center">
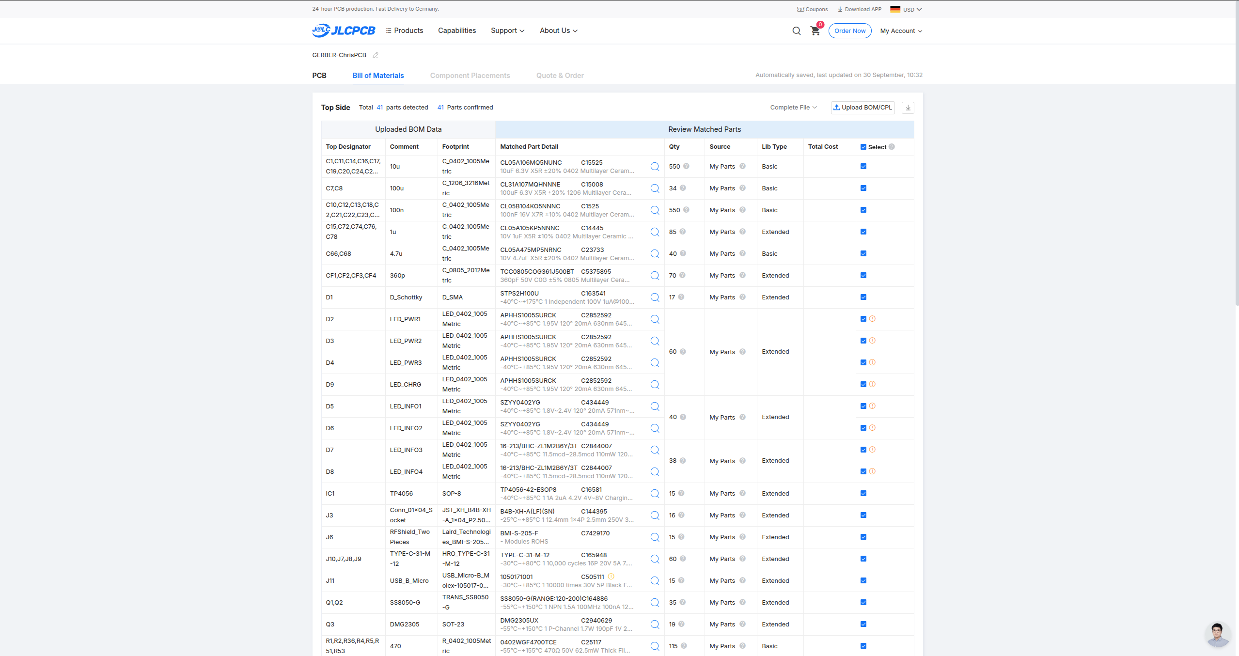
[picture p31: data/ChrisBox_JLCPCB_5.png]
      
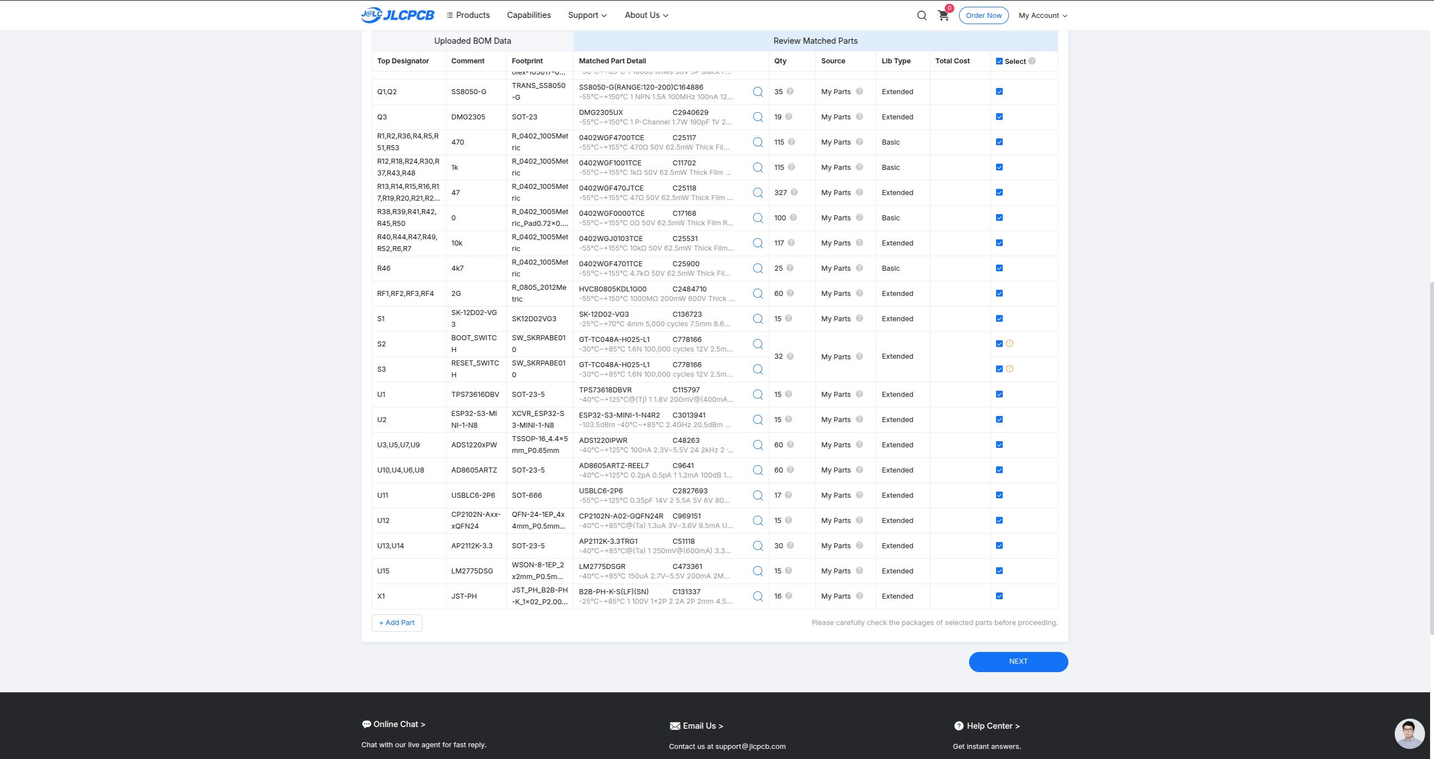
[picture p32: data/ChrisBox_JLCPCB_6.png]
      
</p>

<p align="center">
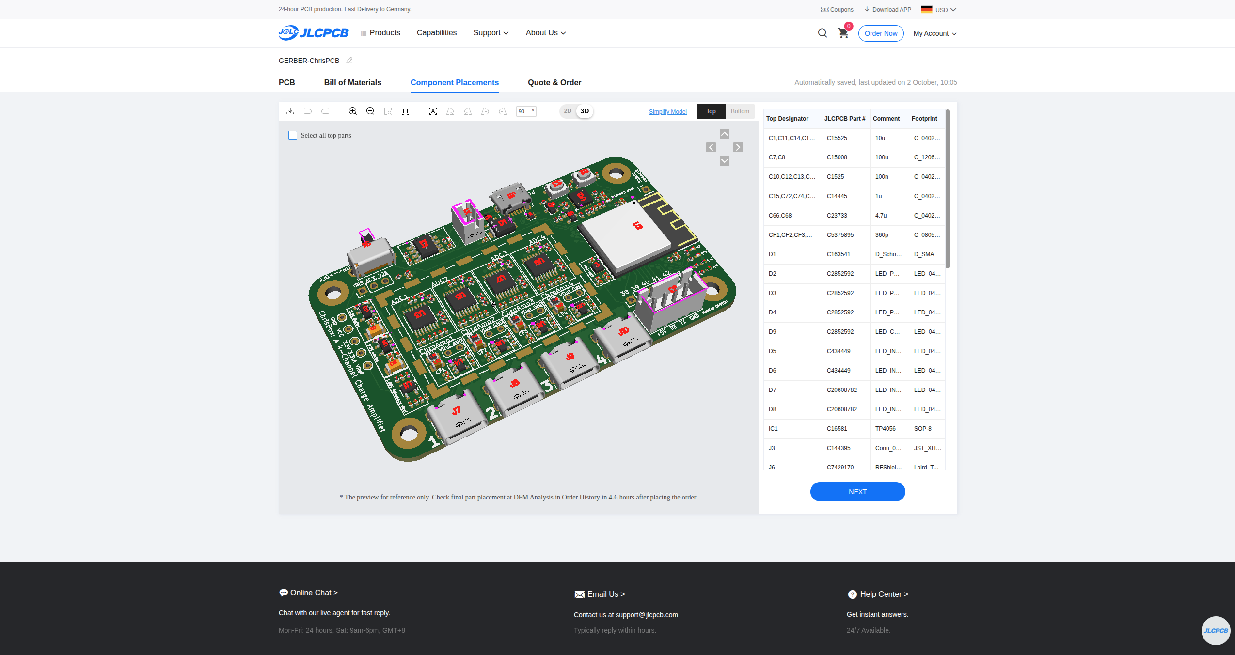
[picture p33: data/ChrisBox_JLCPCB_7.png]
      
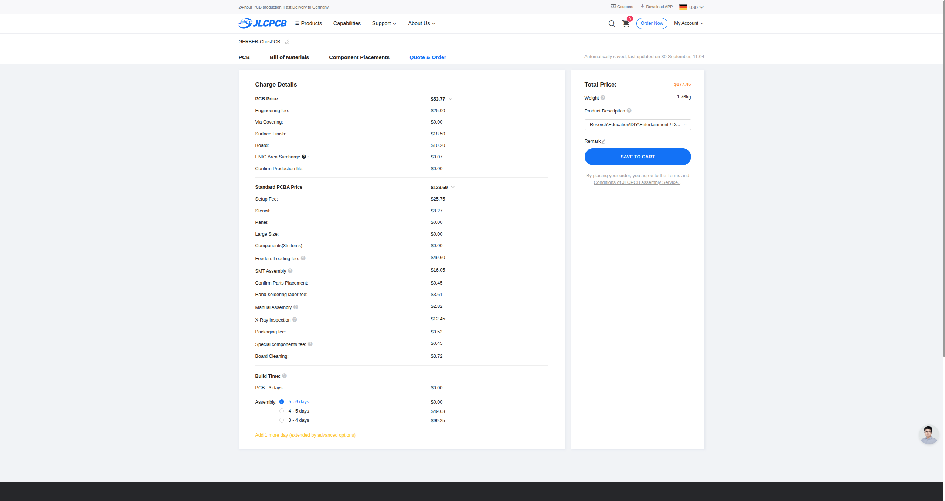
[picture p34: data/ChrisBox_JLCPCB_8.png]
      
</p>

## Additional Required Parts

### Parts for PCB

- [**4x Resistor 5G&Omega;**](https://www.digikey.com/en/products/detail/te-connectivity-passive-product/RH73W2A5GNTN/2366071), footprint 0805 (RH73W2A5GNTN, TE Connectivity).
The value of the feedback resistor decides about the low cutoff frequency of the charge amplifier.
Feel free to choose different values here if other frequencies are required.
- [**1x BMI-S-205-F**](https://www.digikey.com/en/products/detail/laird-technologies-emi/bmi-s-205-f/2175892
) and [**1x BMI-S-205-C**](https://www.digikey.com/en/products/detail/laird-technologies-emi/bmi-s-205-c/2175918
) (Shield Laird Technologies, F for frame, C for cover).
These are two different pieces, one to be soldered on the PCB, the other to be stacked above.

### Parts for Basic Measurement Setup

- [**4x USB-C cable**](https://www.amazon.de/Amazon-Basics-USB-Type-Cable-White/dp/B01GGKZ0V6/) to connect up to four sensors to the PCB
- [**USB-C female connectors/adapters**](https://www.amazon.de/PENGLIN-Stecker-Adapter-Dr%C3%A4hten-Support-Modul/dp/B09YLVSPQX/) for sensors (number depending on the amount of sensors you work with). Important is USB 2.0 functionality, which means that there are D+ and D- connections to solder the ferroelectret to. A shield around the sensor can be soldered to the housing of the adapter.
- [**Micro USB cable**](https://www.amazon.de/Amazon-Basics-%C3%9Cbertragungsgeschwindigkeit-vergoldeten-Steckern/dp/B0711PVX6Z/) to connect the PCB to a PC

## Full ChrisBox Setup

- [**1x Nextion NX3224K024**](https://nextion.tech/datasheets/nx3224k024/) Display
- A 720mAh 3.7V Lithium Polymer battery with JST PH Plug
- 3D prints for the casing (these are probably no parts to be ordered, but to be printed in lab/at home)
- [**4x threaded insert**](https://cnckitchen.store/de/products/heat-set-insert-m3-x-3-short-version-100-pieces) M3 x 3,0 (the CAD has a blind hole of 4mm, and a diameter of 4mm)
- [**4x screw**](https://www.amazon.de/Sechskopf-Knopf-Zylinderschrauben-Gewindeschrauben-Sechskantschrauben-Maschinenschrauben/dp/B0B3MGZ7T2/) M3x25 (the specific choice of screw head is not relevant, but the CAD was theoretically designed for countersunk heads)

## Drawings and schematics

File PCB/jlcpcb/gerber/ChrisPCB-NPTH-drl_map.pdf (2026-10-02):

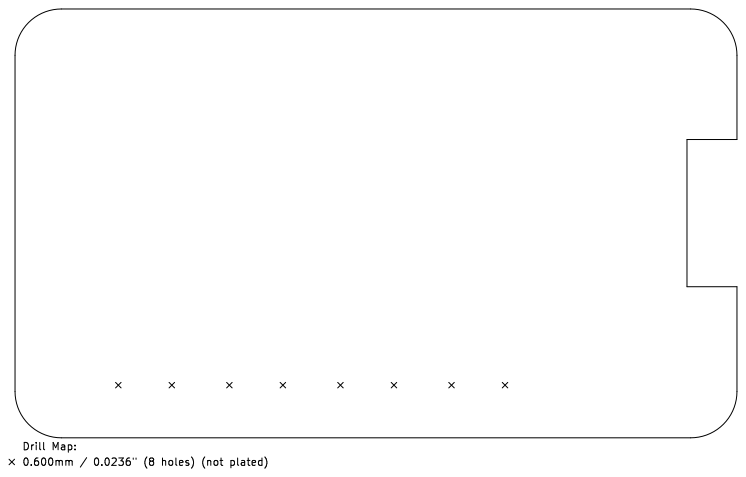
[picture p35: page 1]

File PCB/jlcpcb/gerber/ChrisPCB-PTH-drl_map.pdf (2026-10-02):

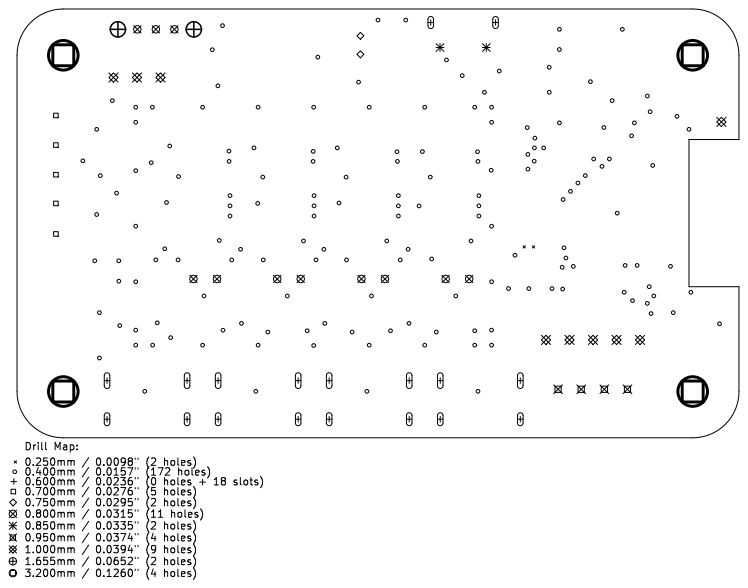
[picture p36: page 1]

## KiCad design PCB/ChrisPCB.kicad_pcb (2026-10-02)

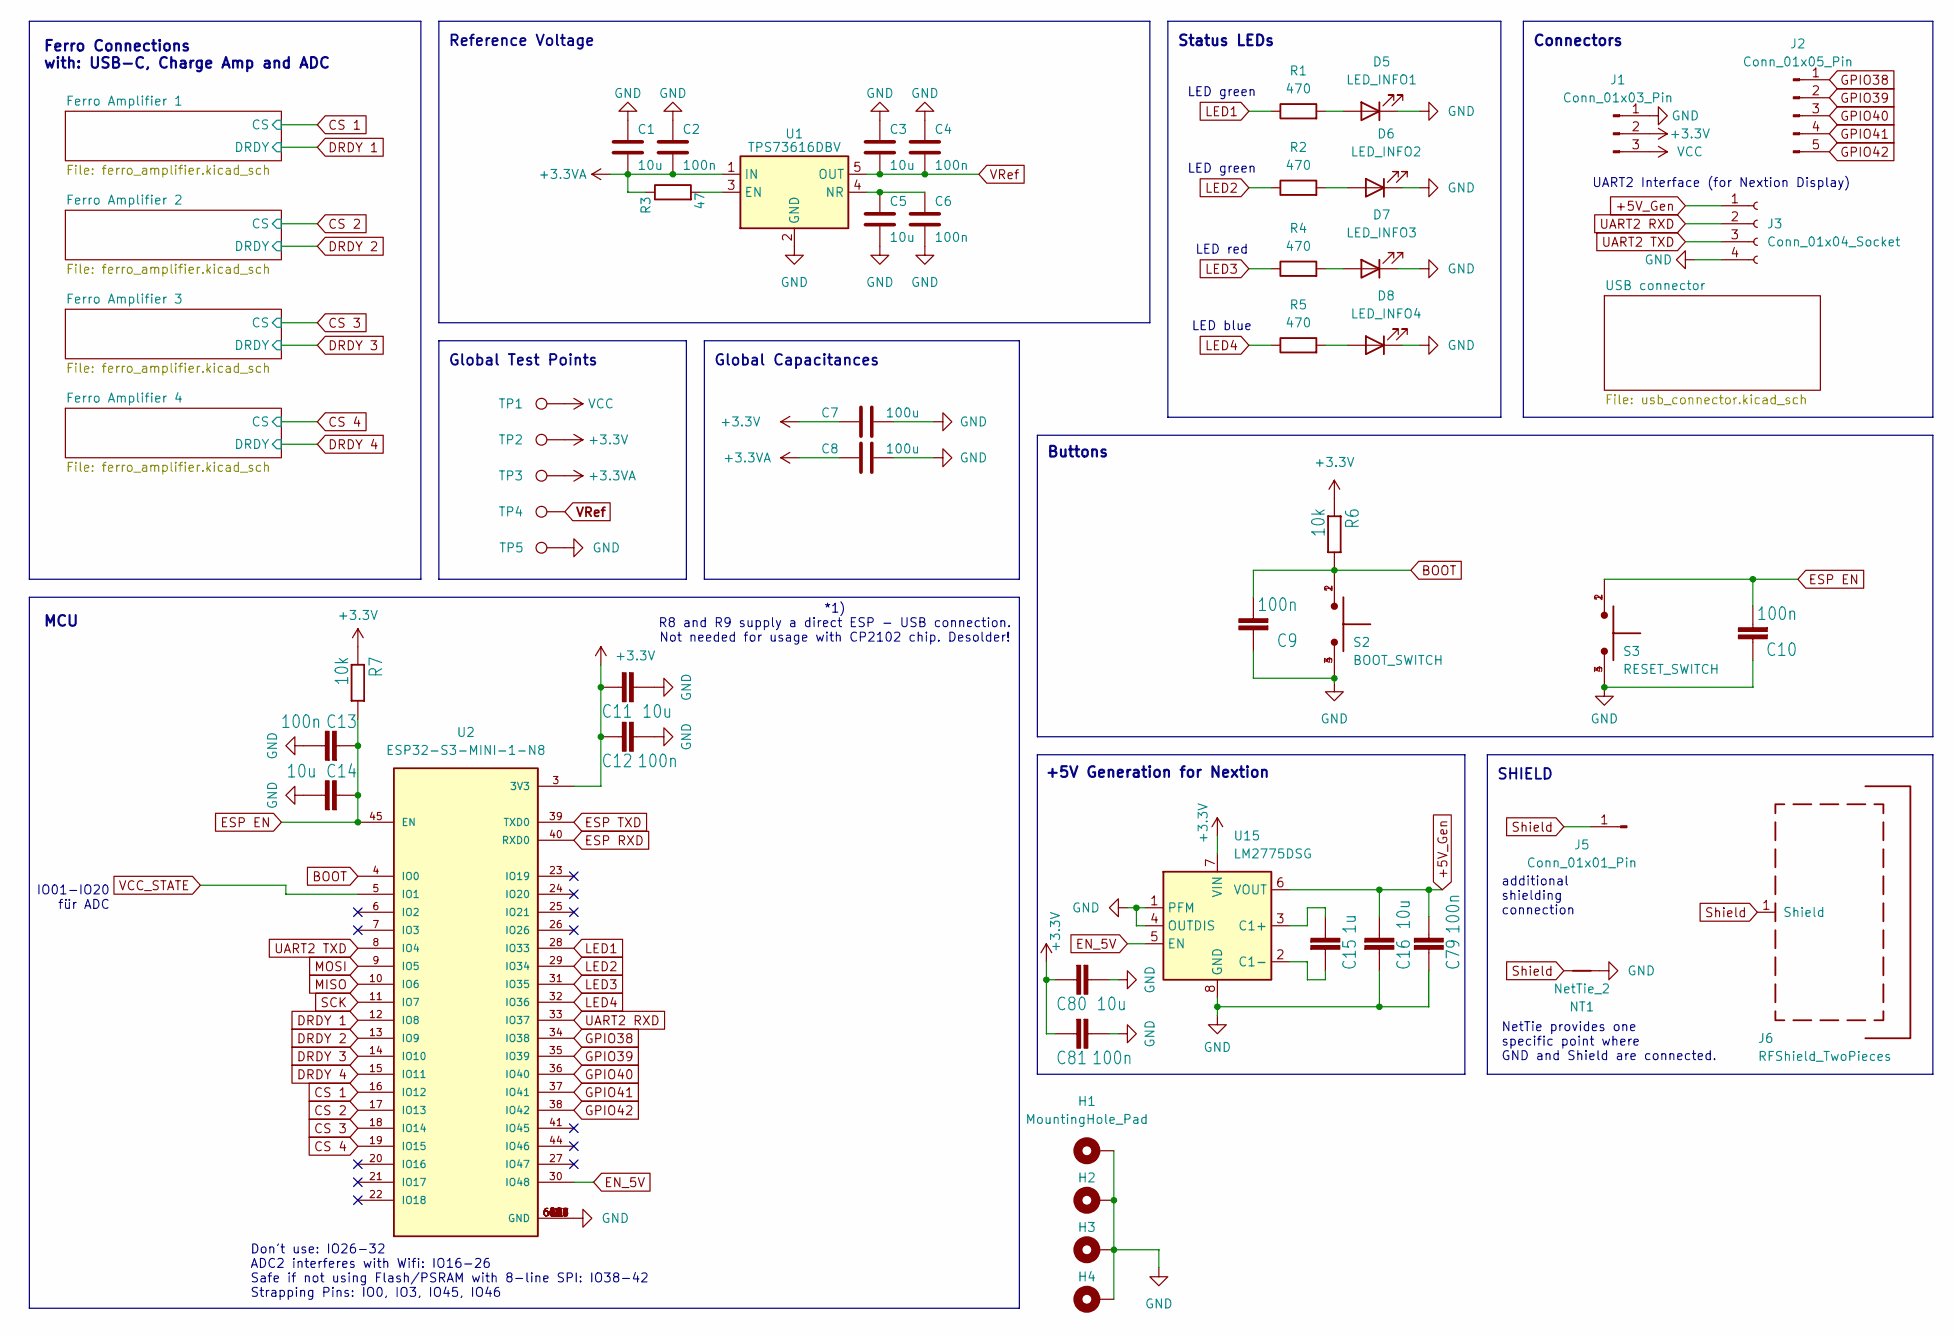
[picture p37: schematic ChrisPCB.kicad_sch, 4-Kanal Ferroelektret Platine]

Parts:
C1, C3, C5, C11, C14, C16, C80: 10u; C_0402_1005Metric
C2, C4, C6, C9, C10, C12, C13, C79, C81: 100n; C_0402_1005Metric
C7, C8: 100u; C_1206_3216Metric
C15: 1u; C_0402_1005Metric
D5: LED_INFO1; LED_0402_1005Metric
D6: LED_INFO2; LED_0402_1005Metric
D7: LED_INFO3; LED_0402_1005Metric
D8: LED_INFO4; LED_0402_1005Metric
H1, H2, H3, H4: MountingHole_Pad; MountingHole_3.2mm_M3_Pad
J1: Conn_01x03_Pin; PinHeader_1x03_P2.54mm_Vertical
J2: Conn_01x05_Pin; PinHeader_1x05_P2.54mm_Vertical
J3: Conn_01x04_Socket; JST_XH_B4B-XH-A_1x04_P2.50mm_Vertical
J5: Conn_01x01_Pin; PinHeader_1x01_P2.54mm_Vertical
J6: RFShield_TwoPieces; Laird_Technologies_BMI-S-205-F_38.10x25.40mm_HandSolder_Sel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
NT1: NetTie_2; NetTie-2_SMD_Pad0.5mm
R1, R2, R4, R5: 470; R_0402_1005Metric
R3: 47; R_0402_1005Metric
R6, R7: 10k; R_0402_1005Metric
S2: BOOT_SWITCH; SW_SKRPABE010
S3: RESET_SWITCH; SW_SKRPABE010
TP1, TP2, TP3, TP4, TP5: TestPoint; TestPoint_THTPad_D1.5mm_Drill0.7mm
U1: TPS73616DBV; SOT-23-5
U2: ESP32-S3-MINI-1-N8; XCVR_ESP32-S3-MINI-1-N8; PARTREV v0.6
U15: LM2775DSG; WSON-8-1EP_2x2mm_P0.5mm_EP0.9x1.6mm_ThermalVias

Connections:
+3.3V: C7.1, C11.2, C12.2, C80.2, C81.2, J1.2, R6.1, R7.1, TP2.1, U2.3 (3V3), U15.7 (VIN); also elsewhere on the board
+3.3VA: C1.2, C2.2, C8.1, R3.1, TP3.1, U1.1 (IN); also elsewhere on the board
+5V_Gen: C16.1, C79.1, J3.1, U15.6 (VOUT)
BOOT: C9.2, R6.2, S2.1, S2.2, U2.4 (IO0); also elsewhere on the board
CS 1: U2.16 (IO12); also elsewhere on the board
CS 2: U2.17 (IO13); also elsewhere on the board
CS 3: U2.18 (IO14); also elsewhere on the board
CS 4: U2.19 (IO15); also elsewhere on the board
DRDY 1: U2.12 (IO8); also elsewhere on the board
DRDY 2: U2.13 (IO9); also elsewhere on the board
DRDY 3: U2.14 (IO10); also elsewhere on the board
DRDY 4: U2.15 (IO11); also elsewhere on the board
EN_5V: U2.30 (IO48), U15.5 (EN)
ESP EN: C10.2, C13.2, C14.2, R7.2, S3.1, S3.2, U2.45 (EN); also elsewhere on the board
ESP RXD: U2.40 (RXD0); also elsewhere on the board
ESP TXD: U2.39 (TXD0); also elsewhere on the board
GND: C1.1, C2.1, C3.1, C4.1, C5.2, C6.2, C7.2, C8.2, C9.1, C10.1, C11.1, C12.1, C13.1, C14.1, C16.2, C79.2, C80.1, C81.1, D5.1 (K), D6.1 (K), D7.1 (K), D8.1 (K), H1.1, H2.1, H3.1, H4.1, J1.1, J3.4, NT1.1, S2.3, S2.4, S3.3, S3.4, TP5.1, U1.2 (GND), U2.1 (GND), U2.2 (GND), U2.42 (GND), U2.43 (GND), U2.46 (GND), U2.47 (GND), U2.48 (GND), U2.49 (GND), U2.50 (GND), U2.51 (GND), U2.52 (GND), U2.53 (GND), U2.54 (GND), U2.55 (GND), U2.56 (GND), U2.57 (GND), U2.58 (GND), U2.59 (GND), U2.60 (GND), U2.61 (GND), U2.61_1 (GND), U2.61_2 (GND), U2.61_3 (GND), U2.61_4 (GND), U2.61_5 (GND), U2.61_6 (GND), U2.61_7 (GND), U2.61_8 (GND), U2.62 (GND), U2.63 (GND), U2.64 (GND), U2.65 (GND), U15.1 (PFM), U15.4 (OUTDIS), U15.8 (GND), U15.9 (GND); also elsewhere on the board
GPIO38: J2.1, U2.34 (IO38)
GPIO39: J2.2, U2.35 (IO39)
GPIO40: J2.3, U2.36 (IO40)
GPIO41: J2.4, U2.37 (IO41)
GPIO42: J2.5, U2.38 (IO42)
LED1: R1.1, U2.28 (IO33)
LED2: R2.1, U2.29 (IO34)
LED3: R4.1, U2.31 (IO35)
LED4: R5.1, U2.32 (IO36)
MISO: U2.10 (IO6); also elsewhere on the board
MOSI: U2.9 (IO5); also elsewhere on the board
unnamed: D5.2 (A), R1.2
unnamed: D6.2 (A), R2.2
unnamed: D7.2 (A), R4.2
unnamed: D8.2 (A), R5.2
unnamed: R3.2, U1.3 (EN)
unnamed: C5.1, C6.1, U1.4 (NR)
unnamed: C15.1, U15.3 (C1+)
unnamed: C15.2, U15.2 (C1-)
SCK: U2.11 (IO7); also elsewhere on the board
Shield: J5.1, J6.1 (Shield), NT1.2; also elsewhere on the board
UART2 RXD: J3.2, U2.33 (IO37)
UART2 TXD: J3.3, U2.8 (IO4)
VCC: J1.3, TP1.1; also elsewhere on the board
VCC_STATE: U2.5 (IO1); also elsewhere on the board
VRef: C3.2, C4.2, TP4.1, U1.5 (OUT); also elsewhere on the board

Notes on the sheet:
+5V Generation for Nextion
Global Capacitances
Global Test Points
Buttons
LED green
Reference Voltage
Ferro Connections with: USB-C, Charge Amp and ADC
NetTie provides one specific point where GND and Shield are connected.
Status LEDs
IO01-IO20 für ADC
MCU
SHIELD
Don't use: IO26-32 ADC2 interferes with Wifi: IO16-26 Safe if not using Flash/PSRAM with 8-line SPI: IO38-42 Strapping Pins: IO0, IO3, IO45, IO46
additional shielding connection
LED blue
*1) R8 and R9 supply a direct ESP - USB connection. Not needed for usage with CP2102 chip. Desolder!
Connectors
LED red
UART2 Interface (for Nextion Display)

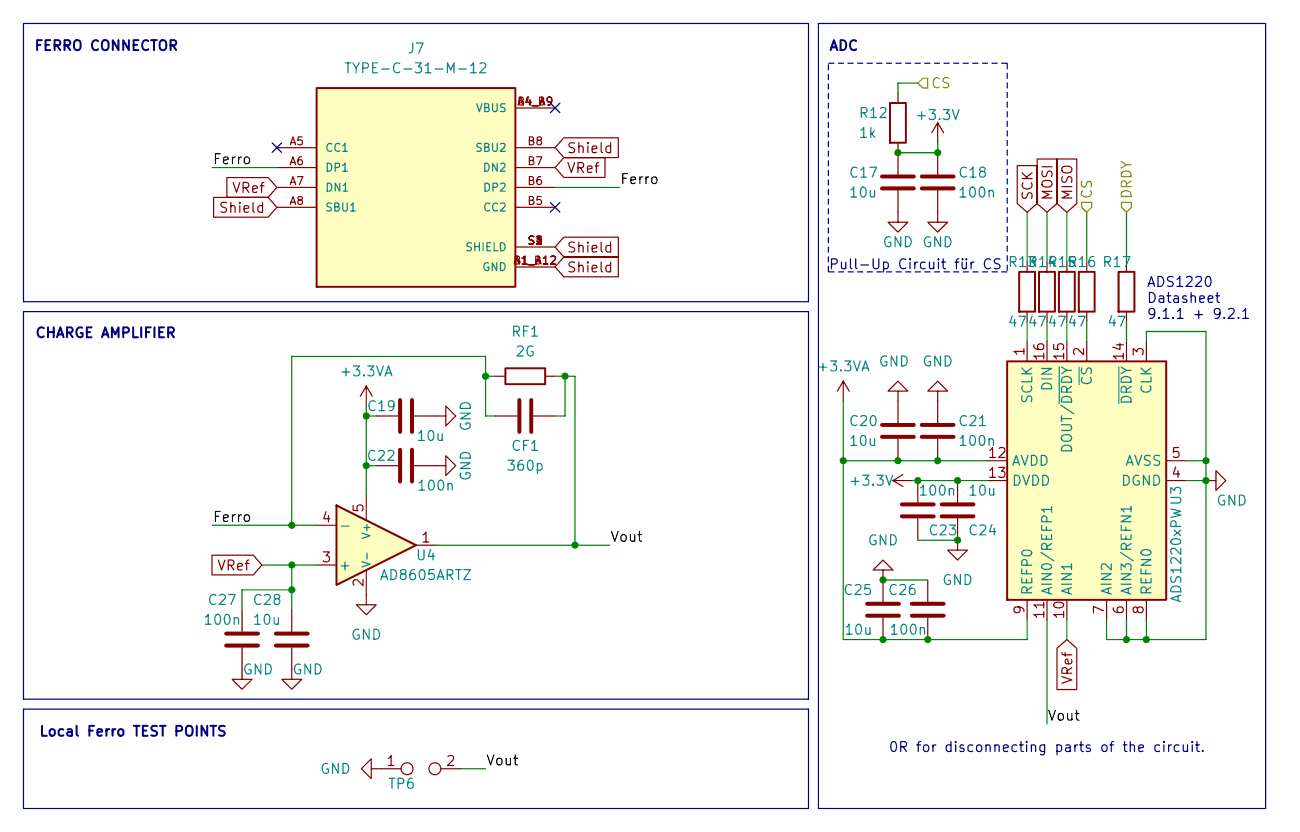
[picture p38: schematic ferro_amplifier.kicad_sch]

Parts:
C17, C19, C20, C24, C25, C28: 10u; C_0402_1005Metric
C18, C21, C22, C23, C26, C27: 100n; C_0402_1005Metric
CF1: 360p; C_0805_2012Metric
J7: TYPE-C-31-M-12; HRO_TYPE-C-31-M-12; PARTREV 2020.12.08
R12: 1k; R_0402_1005Metric
R13, R14, R15, R16, R17: 47; R_0402_1005Metric
RF1: 2G; R_0805_2012Metric
TP6: TestPoint_2Pole; TestPoint_2Pads_Pitch2.54mm_Drill0.8mm
U3: ADS1220xPW; TSSOP-16_4.4x5mm_P0.65mm
U4: AD8605ARTZ; SOT-23-5

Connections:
+3.3V: C17.1, C18.2, C23.2, C24.1, R12.2, U3.13 (DVDD); also elsewhere on the board
+3.3VA: C19.2, C20.2, C21.1, C22.1, C25.1, C26.2, U3.9 (REFP0), U3.12 (AVDD), U4.5 (V+); also elsewhere on the board
/Ferro Amplifier 1/Ferro: CF1.1, J7.A6 (DP1), J7.B6 (DP2), RF1.1, U4.4 (-)
/Ferro Amplifier 1/Vout: CF1.2, RF1.2, TP6.2, U3.11 (AIN0/REFP1), U4.1
CS 1: R12.1, R16.1; also elsewhere on the board
DRDY 1: R17.1; also elsewhere on the board
GND: C17.2, C18.1, C19.1, C20.1, C21.2, C22.2, C23.1, C24.2, C25.2, C26.1, C27.1, C28.2, TP6.1, U3.3 (CLK), U3.4 (DGND), U3.5 (AVSS), U3.6 (AIN3/REFN1), U3.7 (AIN2), U3.8 (REFN0), U4.2 (V-); also elsewhere on the board
MISO: R15.1; also elsewhere on the board
MOSI: R14.1; also elsewhere on the board
unnamed: R14.2, U3.16 (DIN)
unnamed: R15.2, U3.15 (DOUT/~DRDY)
unnamed: R13.2, U3.1 (SCLK)
unnamed: R16.2, U3.2 (~CS)
unnamed: R17.2, U3.14 (~DRDY)
SCK: R13.1; also elsewhere on the board
Shield: J7.A1_B12 (GND), J7.A8 (SBU1), J7.B1_A12 (GND), J7.B8 (SBU2), J7.S1 (SHIELD), J7.S2 (SHIELD), J7.S3 (SHIELD), J7.S4 (SHIELD); also elsewhere on the board
VRef: C27.2, C28.1, J7.A7 (DN1), J7.B7 (DN2), U3.10 (AIN1), U4.3 (+); also elsewhere on the board

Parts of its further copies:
C29, C31, C32, C36, C37, C40, C41, C43, C44, C48, C49, C52, C53, C55, C56, C60, C61, C64: 10u; C_0402_1005Metric
C30, C33, C34, C35, C38, C39, C42, C45, C46, C47, C50, C51, C54, C57, C58, C59, C62, C63: 100n; C_0402_1005Metric
CF2, CF3, CF4: 360p; C_0805_2012Metric
J8, J9, J10: TYPE-C-31-M-12; HRO_TYPE-C-31-M-12; PARTREV 2020.12.08
R18, R24, R30: 1k; R_0402_1005Metric
R19, R20, R21, R22, R23, R25, R26, R27, R28, R29, R31, R32, R33, R34, R35: 47; R_0402_1005Metric
RF2, RF3, RF4: 2G; R_0805_2012Metric
TP7, TP8, TP9: TestPoint_2Pole; TestPoint_2Pads_Pitch2.54mm_Drill0.8mm
U5, U7, U9: ADS1220xPW; TSSOP-16_4.4x5mm_P0.65mm
U6, U8, U10: AD8605ARTZ; SOT-23-5

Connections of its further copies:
+3.3V: C29.1, C30.2, C35.2, C36.1, C41.1, C42.2, C47.2, C48.1, C53.1, C54.2, C59.2, C60.1, R18.2, R24.2, R30.2, U5.13 (DVDD), U7.13 (DVDD), U9.13 (DVDD); also elsewhere on the board
+3.3VA: C31.2, C32.2, C33.1, C34.1, C37.1, C38.2, C43.2, C44.2, C45.1, C46.1, C49.1, C50.2, C55.2, C56.2, C57.1, C58.1, C61.1, C62.2, U5.9 (REFP0), U5.12 (AVDD), U6.5 (V+), U7.9 (REFP0), U7.12 (AVDD), U8.5 (V+), U9.9 (REFP0), U9.12 (AVDD), U10.5 (V+); also elsewhere on the board
/Ferro Amplifier 2/Ferro: CF2.1, J8.A6 (DP1), J8.B6 (DP2), RF2.1, U6.4 (-)
/Ferro Amplifier 2/Vout: CF2.2, RF2.2, TP7.2, U5.11 (AIN0/REFP1), U6.1
/Ferro Amplifier 3/Ferro: CF3.1, J9.A6 (DP1), J9.B6 (DP2), RF3.1, U8.4 (-)
/Ferro Amplifier 3/Vout: CF3.2, RF3.2, TP8.2, U7.11 (AIN0/REFP1), U8.1
/Ferro Amplifier 4/Ferro: CF4.1, J10.A6 (DP1), J10.B6 (DP2), RF4.1, U10.4 (-)
/Ferro Amplifier 4/Vout: CF4.2, RF4.2, TP9.2, U9.11 (AIN0/REFP1), U10.1
CS 2: R18.1, R22.1; also elsewhere on the board
CS 3: R24.1, R28.1; also elsewhere on the board
CS 4: R30.1, R34.1; also elsewhere on the board
DRDY 2: R23.1; also elsewhere on the board
DRDY 3: R29.1; also elsewhere on the board
DRDY 4: R35.1; also elsewhere on the board
GND: C29.2, C30.1, C31.1, C32.1, C33.2, C34.2, C35.1, C36.2, C37.2, C38.1, C39.1, C40.2, C41.2, C42.1, C43.1, C44.1, C45.2, C46.2, C47.1, C48.2, C49.2, C50.1, C51.1, C52.2, C53.2, C54.1, C55.1, C56.1, C57.2, C58.2, C59.1, C60.2, C61.2, C62.1, C63.1, C64.2, TP7.1, TP8.1, TP9.1, U5.3 (CLK), U5.4 (DGND), U5.5 (AVSS), U5.6 (AIN3/REFN1), U5.7 (AIN2), U5.8 (REFN0), U6.2 (V-), U7.3 (CLK), U7.4 (DGND), U7.5 (AVSS), U7.6 (AIN3/REFN1), U7.7 (AIN2), U7.8 (REFN0), U8.2 (V-), U9.3 (CLK), U9.4 (DGND), U9.5 (AVSS), U9.6 (AIN3/REFN1), U9.7 (AIN2), U9.8 (REFN0), U10.2 (V-); also elsewhere on the board
MISO: R21.1, R27.1, R33.1; also elsewhere on the board
MOSI: R20.1, R26.1, R32.1; also elsewhere on the board
unnamed: R20.2, U5.16 (DIN)
unnamed: R21.2, U5.15 (DOUT/~DRDY)
unnamed: R19.2, U5.1 (SCLK)
unnamed: R22.2, U5.2 (~CS)
unnamed: R23.2, U5.14 (~DRDY)
unnamed: R26.2, U7.16 (DIN)
unnamed: R27.2, U7.15 (DOUT/~DRDY)
unnamed: R25.2, U7.1 (SCLK)
unnamed: R28.2, U7.2 (~CS)
unnamed: R29.2, U7.14 (~DRDY)
unnamed: R32.2, U9.16 (DIN)
unnamed: R33.2, U9.15 (DOUT/~DRDY)
unnamed: R31.2, U9.1 (SCLK)
unnamed: R34.2, U9.2 (~CS)
unnamed: R35.2, U9.14 (~DRDY)
SCK: R19.1, R25.1, R31.1; also elsewhere on the board
Shield: J8.A1_B12 (GND), J8.A8 (SBU1), J8.B1_A12 (GND), J8.B8 (SBU2), J8.S1 (SHIELD), J8.S2 (SHIELD), J8.S3 (SHIELD), J8.S4 (SHIELD), J9.A1_B12 (GND), J9.A8 (SBU1), J9.B1_A12 (GND), J9.B8 (SBU2), J9.S1 (SHIELD), J9.S2 (SHIELD), J9.S3 (SHIELD), J9.S4 (SHIELD), J10.A1_B12 (GND), J10.A8 (SBU1), J10.B1_A12 (GND), J10.B8 (SBU2), J10.S1 (SHIELD), J10.S2 (SHIELD), J10.S3 (SHIELD), J10.S4 (SHIELD); also elsewhere on the board
VRef: C39.2, C40.1, C51.2, C52.1, C63.2, C64.1, J8.A7 (DN1), J8.B7 (DN2), J9.A7 (DN1), J9.B7 (DN2), J10.A7 (DN1), J10.B7 (DN2), U5.10 (AIN1), U6.3 (+), U7.10 (AIN1), U8.3 (+), U9.10 (AIN1), U10.3 (+); also elsewhere on the board

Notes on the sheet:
0R for disconnecting parts of the circuit.
Pull-Up Circuit für CS
CHARGE AMPLIFIER
ADS1220 Datasheet 9.1.1 + 9.2.1
ADC
Local Ferro TEST POINTS
FERRO CONNECTOR

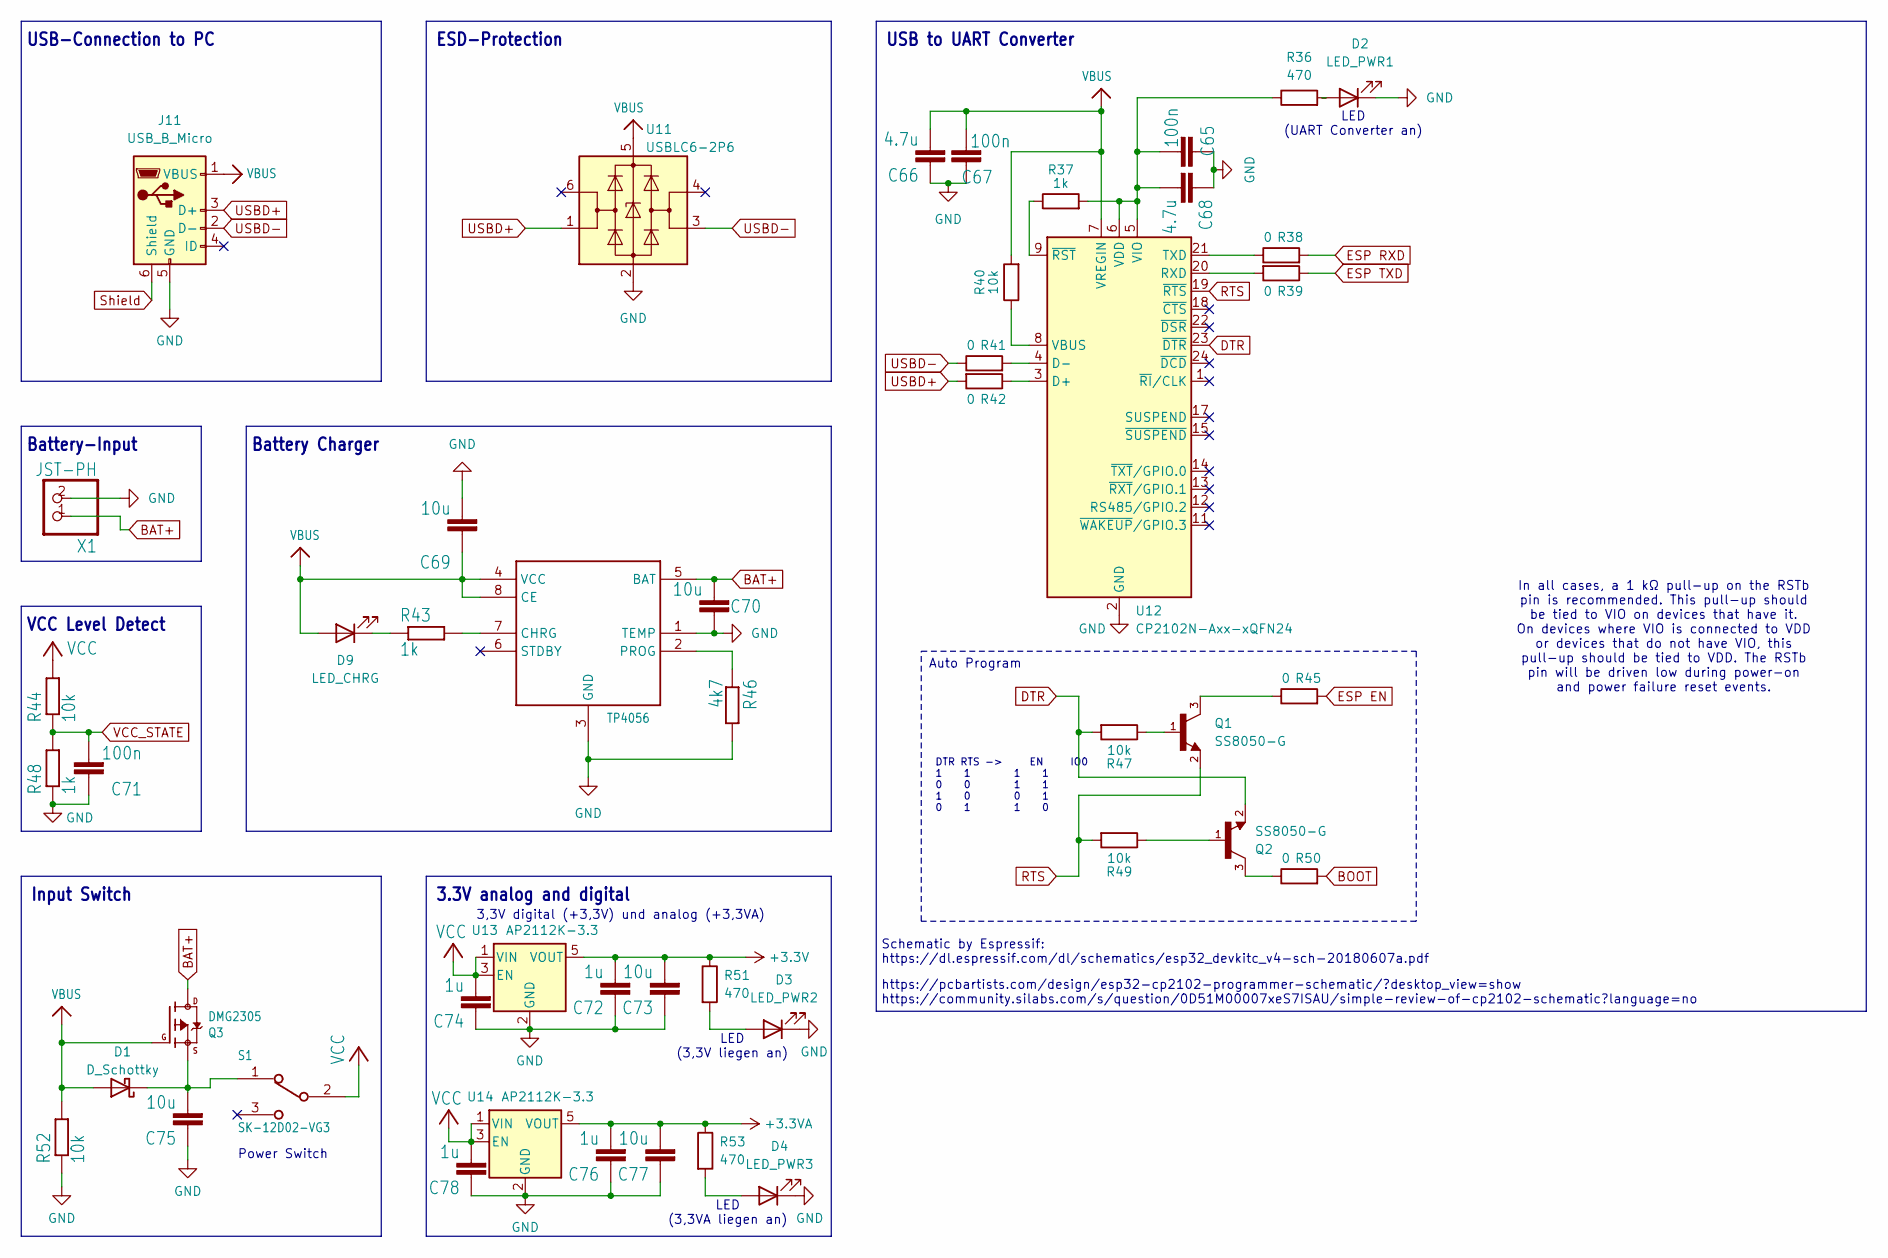
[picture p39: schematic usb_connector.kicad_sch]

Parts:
C65, C67, C71: 100n; C_0402_1005Metric
C66, C68: 4.7u; C_0402_1005Metric
C69, C70, C73, C75, C77: 10u; C_0402_1005Metric
C72, C74, C76, C78: 1u; C_0402_1005Metric
D1: D_Schottky; D_SMA
D2: LED_PWR1; LED_0402_1005Metric
D3: LED_PWR2; LED_0402_1005Metric
D4: LED_PWR3; LED_0402_1005Metric
D9: LED_CHRG; LED_0402_1005Metric
IC1: TP4056; SOP-8
J11: USB_B_Micro; USB_Micro-B_Molex-105017-0001
Q1, Q2: SS8050-G; TRANS_SS8050-G; PARTREV A
Q3: DMG2305; SOT-23
R36, R51, R53: 470; R_0402_1005Metric
R37, R43, R48: 1k; R_0402_1005Metric
R38, R39, R41, R42, R45, R50: 0; R_0402_1005Metric_Pad0.72x0.64mm_HandSolder
R40, R44, R47, R49, R52: 10k; R_0402_1005Metric
R46: 4k7; R_0402_1005Metric
S1: SK-12D02-VG3; SK12D02VG3
U11: USBLC6-2P6; SOT-666
U12: CP2102N-Axx-xQFN24; QFN-24-1EP_4x4mm_P0.5mm_EP2.6x2.6mm
U13, U14: AP2112K-3.3; SOT-23-5
X1: JST-PH; JST_PH_B2B-PH-K_1x02_P2.00mm_Vertical

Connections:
+3.3V: C72.2, C73.2, R51.1, U13.5 (VOUT); also elsewhere on the board
+3.3VA: C76.2, C77.2, R53.1, U14.5 (VOUT); also elsewhere on the board
BAT+: C70.2, IC1.5 (BAT), Q3.3 (D), X1.1
BOOT: R50.2; also elsewhere on the board
DTR: Q2.2, R47.2, U12.23 (~DTR)
ESP EN: R45.2; also elsewhere on the board
ESP RXD: R38.2; also elsewhere on the board
ESP TXD: R39.1; also elsewhere on the board
GND: C65.1, C66.1, C67.1, C68.1, C69.2, C70.1, C71.1, C72.1, C73.1, C74.1, C75.1, C76.1, C77.1, C78.1, D2.1 (K), D3.1 (K), D4.1 (K), IC1.1 (TEMP), IC1.3 (GND), J11.5 (GND), R46.2, R48.1, R52.1, U11.2 (GND), U12.2 (GND), U12.25 (GND), U13.2 (GND), U14.2 (GND), X1.2; also elsewhere on the board
unnamed: C75.2, D1.1 (K), Q3.2 (S), S1.1
unnamed: D2.2 (A), R36.2
unnamed: D3.2 (A), R51.2
unnamed: D4.2 (A), R53.2
unnamed: D9.1 (K), R43.1
unnamed: IC1.7 (CHRG), R43.2
unnamed: IC1.2 (PROG), R46.1
unnamed: Q1.1, R47.1
unnamed: Q1.3, R45.1
unnamed: Q2.1, R49.1
unnamed: Q2.3, R50.1
unnamed: R42.1, U12.3 (D+)
unnamed: R41.2, U12.4 (D-)
unnamed: R39.2, U12.20 (RXD)
unnamed: R38.1, U12.21 (TXD)
unnamed: R40.1, U12.8 (VBUS)
unnamed: C65.2, C68.2, R36.1, R37.2, U12.5 (VIO), U12.6 (VDD)
unnamed: R37.1, U12.9 (~RST)
RTS: Q1.2, R49.2, U12.19 (~RTS)
Shield: J11.6 (Shield); also elsewhere on the board
USBD+: J11.3 (D+), R42.2, U11.1 (I/O1)
USBD-: J11.2 (D-), R41.1, U11.3 (I/O2)
VBUS: C66.2, C67.2, C69.1, D1.2 (A), D9.2 (A), IC1.4 (VCC), IC1.8 (CE), J11.1 (VBUS), Q3.1 (G), R40.2, R52.2, U11.5 (VBUS), U12.7 (VREGIN)
VCC: C74.2, C78.2, R44.2, S1.2, U13.1 (VIN), U13.3 (EN), U14.1 (VIN), U14.3 (EN); also elsewhere on the board
VCC_STATE: C71.2, R44.1, R48.2; also elsewhere on the board

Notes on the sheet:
LED (UART Converter an)
Battery Charger
USB-Connection to PC
Auto Program
VCC Level Detect
LED (3,3V liegen an)
3,3V digital (+3,3V) und analog (+3,3VA)
Power Switch
In all cases, a 1 kΩ pull-up on the RSTb pin is recommended. This pull-up should be tied to VIO on devices that have it. On devices where VIO is connected to VDD or devices that do not have VIO, this pull-up should be tied to VDD. The RSTb pin will be driven low during power-on and power failure re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
USB to UART Converter
3.3V analog and digital
DTR RTS -> EN IO0 1 1 1 1 0 0 1 1 1 0 0 1 0 1 1 0
Battery-Input
ESD-Protection
LED (3,3VA liegen an)
Input Switch
Schematic by Espressif: https://dl.espressif.com/dl/schematics/esp32_devkitc_v4-sch-20180607a.pdf
https://pcbartists.com/design/esp32-cp2102-programmer-schematic/?desktop_view=show https://community.silabs.com/s/question/0D51M00007xeS7ISAU/simple-review-of-cp2102-schematic?language=no

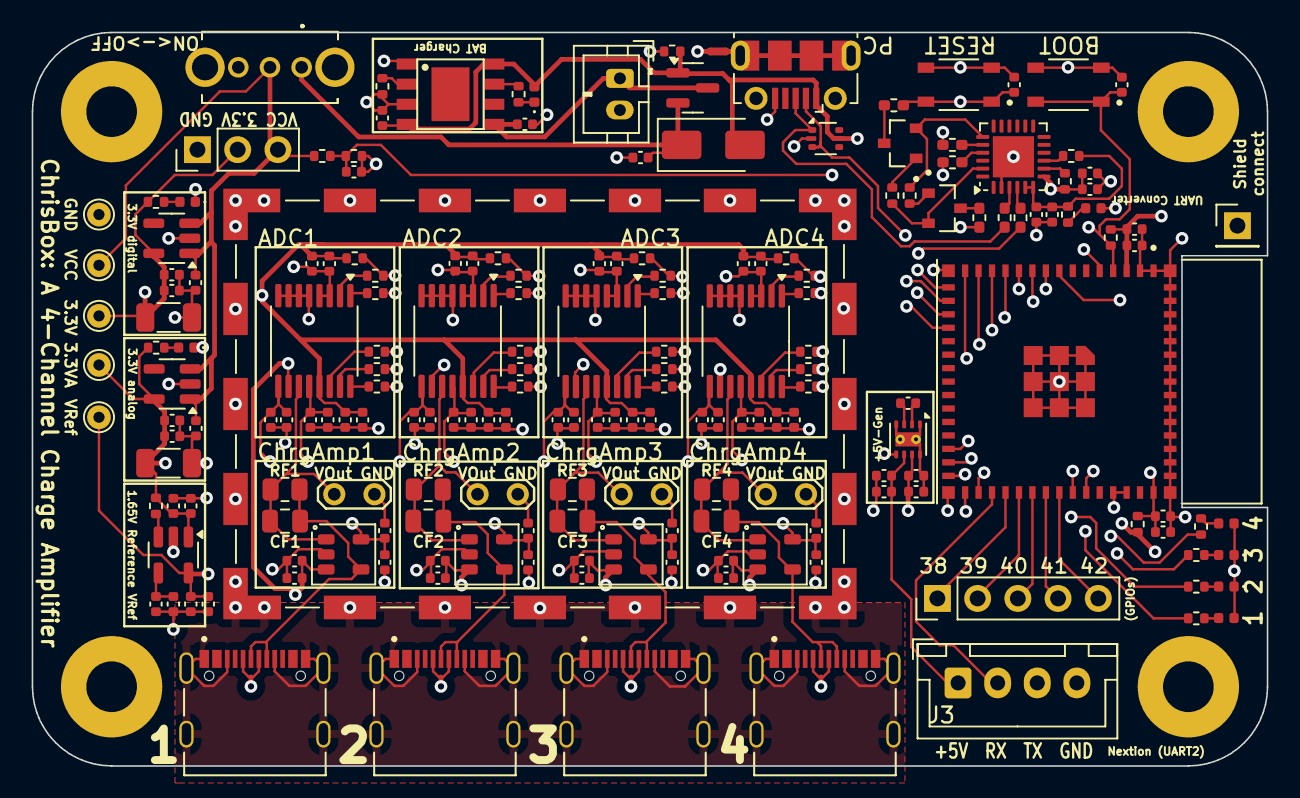
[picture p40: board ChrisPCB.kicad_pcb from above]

Board: 4 copper layers, 78.0 x 46.3 mm, 194 parts (0 on the bottom side), 95 nets.

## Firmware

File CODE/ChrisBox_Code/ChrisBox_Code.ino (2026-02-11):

/*
  ChrisBox_Code.ino - Code for the ChrisBox - a multi-channel ferroelectret measurement device
  @authors Dominik Werner and Luis Gross
  @date   2026-02-04
  @version 1.1
  at MUST-TU Darmstadt, Germany
*/
//-------------------------------------------------------------------------------------------------------------------
// Include Libraries
#include <esp_now.h>                  // for ESP NOW communication
#include <WiFi.h>                     // for ESP NOW communication
#include <ADS1220_WE.h>                      // for ADS1220 communication

//-------------------------------------------------------------------------------------------------------------------
// Define Pins

// ADS1220 (4x)
int CS_Pins[] = {12, 13, 14, 15};
int DRDY_Pins[] = {8, 9, 10, 11};
#define SCK     7   // SPI Clock
#define MISO    6   // SPI MISO
#define MOSI    5   // SPI MOSI

// LEDs
#define LED1 33   // LED Green    -> status indicator if program is working
#define LED2 34   // LED Green    -> battery status indicator, blinking if VCC is below a threshold
#define LED3 35   // LED Blue     -> status indicator if UART2 is connected/working
#define LED4 36   // LED Blue     -> status indicator if ESP NOW is connected

#define VCC 1       // VCC, measured with internal ADC of ESP32

// UART2 Pins
#define UART2TXD 4  
#define UART2RXD 37

// 5V generation enable
#define EN_5V 48

//-------------------------------------------------------------------------------------------------------------------
// Settings and constants

uint8_t broadcastAddress1[] = {0x08, 0x3a, 0xf2, 0xb9, 0x02, 0x40};   // REPLACE WITH YOUR ESP RECEIVER'S MAC ADDRESS

bool display_charge = true;    // Decide if the charge value shall be displayed (true) or the voltage value (false) on the Nextion display
bool esp_now_connection = false;  // Decide if ESPNOW connection shall be used or not (required for ESP to ESP wireless connection)
bool uart2_connection = true;     // Decide if UART2 shall be used (required for Nextion display)
bool voltage_generation = true;   // Decide if the 5V voltage generation should work (required for Nextion display)

#define UART2BAUD 115200          // Define the baud rate for UART2 communication

#define CF 360                    // Feedback capacitance [pF] (Q = C * U, Charge = CF * Voltage)

#define thresVCC 3.2              // Threshold for VCC, where the battery indicator should start blinking (ESP 32 recommended minimum voltage is 3.0V)
  
#define VREFADC  3.28         // ADS1220, Reference voltage
#define NUM_ADCS 4
//-------------------------------------------------------------------------------------------------------------------
// Variables

int lastBlink;                // time of last blink for LED1 blinking
int lastBlinkBattery;         // time of last blink for Battery Warning LED2
bool uartConnected;           // marker wheter UART2 is connected or not -> shown by blue LED3
bool espNowConnected;         // marker whether ESP NOW is connected -> shown by blue LED4
bool batteryAlert;            // marker if the voltage is too low
double vRef_mV;             // measured VRef in millivolt
double maxVoltagePlus;        // maximum voltage for positive charge calculation
double maxChargePlus;         // maximum charge for positive charge calculation
double maxVoltageMinus;       // maximum voltage for negative charge calculation
double maxChargeMinus;        // maximum charge for negative charge calculation


ADS1220_WE adc[NUM_ADCS] = {
  ADS1220_WE(&SPI, CS_Pins[0], DRDY_Pins[0], MOSI, MISO, SCK, true, false),
  ADS1220_WE(&SPI, CS_Pins[1], DRDY_Pins[1], MOSI, MISO, SCK, true, false),
  ADS1220_WE(&SPI, CS_Pins[2], DRDY_Pins[2], MOSI, MISO, SCK, true, false),
  ADS1220_WE(&SPI, CS_Pins[3], DRDY_Pins[3], MOSI, MISO, SCK, true, false)
};  // Four ADCs...
float adc_data[4];          // ... and a place to store their readings

int displayPage = 0;              // display page as int. 1 is the first page, 7 the last one.

// Struct, in which all measurement data is stored
typedef struct four_ch_struct {
  double vcc;
  double vref;
  double ferro1;
  double ferro2;
  double ferro3;
  double ferro4;
} four_ch_struct;

four_ch_struct data_struct;

//-------------------------------------------------------------------------------------------------------------------
// Setup for ESP_NOW
esp_now_peer_info_t peerInfo;

// callback when data is sent
void OnDataSent(const uint8_t *mac_addr, esp_now_send_status_t status) {
  char macStr[18];
  /*
  // Debug Information
  Serial.print("Packet to: ");
  // Copies the sender mac address to a string
  snprintf(macStr, sizeof(macStr), "%02x:%02x:%02x:%02x:%02x:%02x",
          mac_addr[0], mac_addr[1], mac_addr[2], mac_addr[3], mac_addr[4], mac_addr[5]);
  Serial.print(macStr);
  Serial.print(" send status:\t");
  Serial.println(status == ESP_NOW_SEND_SUCCESS ? "Delivery Success" : "Delivery Fail");
  */
}
//-------------------------------------------------------------------------------------------------------------------
// Setup for UART2

// used for display here (NX3224K024)
HardwareSerial displaySerial(2);
String endChar = String(char(0xff)) + String(char(0xff)) + String(char(0xff));

//-------------------------------------------------------------------------------------------------------------------

void setup() {
  Serial.begin(115200);
  Serial.println("Setup started.");

  batteryAlert = false;

  // -------------------------------------------------------
  // 5V generation setup
  pinMode(EN_5V, OUTPUT);         // 5V generation pin is output
  if (voltage_generation) {
    digitalWrite(EN_5V, HIGH);    // 5V shall be generated
    delay(200);                   // Delay that the display or other connected device can start.
  } else {
    digitalWrite(EN_5V, LOW);
  }
  
  // -------------------------------------------------------
  // ESP NOW Start
  espNowConnected = false;

  if (esp_now_connection) {
    WiFi.mode(WIFI_STA);
  
    if (esp_now_init() != ESP_OK) {
      Serial.println("Error initializing ESP-NOW");
      espNowConnected = false;
    } else {
      espNowConnected = true;
    }
    
    // esp_now_register_send_cb(OnDataSent); //Produces Errors
    
    // register peer
    peerInfo.channel = 0;  
    peerInfo.encrypt = false;
    // register first peer  
    memcpy(peerInfo.peer_addr, broadcastAddress1, 6);
    if (esp_now_add_peer(&peerInfo) != ESP_OK){
      Serial.println("Failed to add peer");
      espNowConnected = false;
    } else {
      espNowConnected = true;
    }
  }
  // -------------------------------------------------------
  // UART2 Connection
  uartConnected = false;

  // If UART2 connection is wished, it is started here.
  if (uart2_connection) {
    displaySerial.begin(UART2BAUD, SERIAL_8N1, UART2RXD, UART2TXD);
    Serial.print("UART2 connection started with baud rate ");
    Serial.println(UART2BAUD);

    displaySerial.print(endChar);                           // Send end Char to start a clean conversation
    displaySerial.print("page Splash" + endChar);   // Send page command to start on the first page.
    displayPage = 1;
  }  

  // -------------------------------------------------------

  pinMode(LED1, OUTPUT);        // LEDs as digital output pins (Program working)
  pinMode(LED2, OUTPUT);        // ...  (Battery Status)
  pinMode(LED3, OUTPUT);        // ...  (UART2 connected)
  pinMode(LED4, OUTPUT);        // ...  (ESP NOW connected)

  startupLEDshow();             // Little lightshow at the start, because it is cool.
  
  setupADCs();
  
  // Initialisieren von Variablen
  vRef_mV = getVRef()*1000;                    // VRef in millivolt
  maxVoltagePlus = 3.3 - (vRef_mV / 1000.0);   // max voltage for display plus 
  maxChargePlus = maxVoltagePlus * CF;         // max voltage plus * feedback capacitance.
  maxVoltageMinus = 0 - (vRef_mV / 1000.0);    // max voltage for display minus
  maxChargeMinus = maxVoltageMinus * CF;       // max voltage minus * feedback capacitance.

  lastBlink = millis();
  lastBlinkBattery = millis();

  Serial.println("Setup finished.");
}

//-------------------------------------------------------------------------------------------------------------------

void loop() {

  refreshLEDs();        // update LEDs for blinking and status etc.
  readoutADCs();        // read ADC data from all four ADCs

  // // Debug
  // adc_data[0] = 3300;
  // adc_data[1] = 0;
  // adc_data[2] = 2000;
  // adc_data[3] = 1000;


  if(displayPage == 7){
    data_struct.vcc = getVCC();                           // read and store VCC (internal ADC)
    data_struct.vref = getVRef();                         // read and store VRef (internal ADC)
  }  
  if(display_charge) {
    // Convert ADC voltage readings to charge values
    data_struct.ferro1 = convertToPicoC(adc_data[0]);    // compute charge of Ferro 1 (ADS1220)
    data_struct.ferro2 = convertToPicoC(adc_data[1]);    // compute charge of Ferro 2(ADS1220)
    data_struct.ferro3 = convertToPicoC(adc_data[2]);    // compute charge of Ferro 3 (ADS1220)
    data_struct.ferro4 = convertToPicoC(adc_data[3]);    // compute charge of Ferro 4 (ADS1220)
  } else {
    // Store ADC voltage readings directly
    data_struct.ferro1 = adc_data[0];    // voltage of Ferro 1 (ADS1220)
    data_struct.ferro2 = adc_data[1];    // voltage of Ferro 2(ADS1220)
    data_struct.ferro3 = adc_data[2];    // voltage of Ferro 3 (ADS1220)
    data_struct.ferro4 = adc_data[3];    // voltage of Ferro 4 (ADS1220)
  }


  // --------------------------------------------------------------------
  // Serial print the measured values
  // -> Serial print should work with BetterSerialPlotter on a PC
  // VCC und VRef
  Serial.print(data_struct.vcc, 6);       // The number (6) indicates how many decimal digits will be shown.
  Serial.print(" ");
  Serial.print(data_struct.vref, 6);
  Serial.print(" ");

  // Four Channel
  Serial.print(data_struct.ferro1, 6);
  Serial.print(" ");
  Serial.print(data_struct.ferro2, 6);
  Serial.print(" ");
  Serial.print(data_struct.ferro3, 6);
  Serial.print(" ");
  Serial.print(data_struct.ferro4, 6);
  Serial.print(" ");
  
  // --------------------------------------------------------------------
  // End print with new line
  Serial.println();

  // --------------------------------------------------------------------
  // Send data via ESPNOW
  if (esp_now_connection) {
    esp_err_t result = esp_now_send(0, (uint8_t *) &data_struct, sizeof(four_ch_struct));
    
    if (result == ESP_OK) {
      Serial.println("Sent with success");
      espNowConnected = true;
    }
    else {
      Serial.println("Error sending the data");
      espNowConnected = false;
    }
  }

  // send data via UART2 (to display)
  if (uart2_connection) {
    uartConnected = true;
    readFromDisplay();
    sendDataToDisplay();
  }
}
// End of loop

//-------------------------------------------------------------------------------------------------------------------

// Calculates the VCC voltage from the analog read of BatState
double getVCC() {
  int batState = analogRead(VCC);
  // Factor 11 from voltage divider
  double vcc = 11 * batState * (3.3 / 4095);
  if (vcc < thresVCC) {
    batteryAlert = true;
  } else {
    batteryAlert = false;
  }
  return vcc;
}

// Measures the VRef voltage from the read of VRef at ADC1
double getVRef() {
  // Do all this only if the VRef is shown on the display, otherwise this just reduces performance.
    adc[0].setCompareChannels(ADS1220_MUX_1_AVSS);
    // adc[0].start(); // ADC Ferro

    // while(digitalRead(DRDY_Pins[0])){}

    double vref_double = adc[0].getVoltage_mV() / 1000;
    adc[0].setCompareChannels(ADS1220_MUX_0_AVSS);

    return vref_double;
  }
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

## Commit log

2025-05-28 Initial push and WIP PCB
    [1050170001.prt, 105017000112647.prt, 1050170001_1_step.prt, 1050170001_step.prt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]
2025-05-28 PCB Routing done
    [ChrisPCB.kicad_pcb]
2025-05-30 Fixed .gitignore, 3D-Models are now included
    [1050170001.stp, 302-S-06-D1R1.step, 302-S-10-D1R1.step, AP2112K-3.3TRG1.step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]
2025-06-02 JLCPCB Tool ausgefüllt
    [BOM-ChrisPCB.csv, CPL-ChrisPCB.csv, ChrisPCB-CuBottom.gbr, ChrisPCB-CuIn1.gbr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]
2025-06-05 Added JST-XH to BOM and Assembly List
    [BOM-ChrisPCB.csv, BOM-Platine 4 Kanal Ferroelektret.csv, CPL-ChrisPCB.csv, CPL-Platine 4 Kanal Ferroelektret.csv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]
2025-06-11 PCB Ordner sortiert
    [ChrisPCB.step, spi_connectors.kicad_sch]
2025-06-11 CAD STLs cleanup
    [Casing_Bottom.stl, Casing_Bottom_1.stl, Casing_Top.stl, Casing_Top_1.stl]
2025-06-11 CAD cleanup
    [1050170001.prt, 105017000112647.prt, 1050170001_1_step.prt, 1050170001_step.prt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]
2025-06-11 Moved screws
    [Screw_ISO_10642_M3x25.prt]
2025-06-11 CAD rename
    [ChrisBox_Assembly.prt, ChrisBox_Casing_Bottom.prt, ChrisBox_Casing_Top.prt, ChrisBox_PCB.prt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]
2025-06-11 PCB folder rename
2025-09-16 Added CAD files for case for use without nextion screen
    [4CH-ESP32-DMS_ChrisBox.step]
2025-10-15 Delete PCB/data directory
    Due to copyright issues
2025-11-06 Polish readme,
    insert parts from paper abstract, harmonize white space and line breaks.
